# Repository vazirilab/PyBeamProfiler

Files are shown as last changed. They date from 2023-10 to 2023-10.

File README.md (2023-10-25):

# PyBeamProfiler
A laser beam profiler app for FLIR cameras to monitor laser beam and control position using stepper motors. The GUI is very easy to use and manipulate and develop. 

## Installation
1. Clone this repository
1. Install any version of the Anaconda Python distribution. We highly recommend [Miniforge](https://github.com/conda-forge/miniforge), which is minimal and fast.
1. Create a new virtual environment using the `mamba` or `conda` command that comes with Anaconda/Miniforge and the supplied `beam_profile.yml` file (top level of the repository): `mamba env create -f beam_profile.yml`
1. Activate the environment: `mamba activate beam_profile`
1. Install the package used to control the FLIR camera `PySpin` by downloading the [Spinnaker SDK library](https://www.flir.com/products/spinnaker-sdk/?vertical=machine+vision&segment=iis).
1. Run the app: `python pybeamprofiler_main.py`

## Features and Usage
- You can either use it to monitor a live stream from a FLIR camera or you can load existing data (images from previous recordings).
- The GUI gives the user control over many parameters like the number of frames or the frame rate. It also allows the user to either set a specific exposure time or change it to be automatically set.
- If the user wants to save the results of a recording, they will have to select the number of frames contained in each .csv file. The first .csv file will be named (user selected name)_0.csv and the number goes up for the next file. The .csv contains the following values: 
  1. the time a frame is acquired. 
  2. The X-position of the center. 
  3. The Y-position of the center. 
  4. The std of the Gaussian distribution of the beam. 
  5. The FWHM of the Gaussian distribution of the beam.
- The profile of the beam can be saved as well by enabling the corresponding checkbox
- If the Saving option is selected while recording from "Position Control", the saved .csv file will contain: 
  1. the timestamp of an  acquired frame.
  2. The X-position of the center. 
  3. The Y-position of the center. 
  4. Loop response in X. 
  5. Loop response in Y. 
  6. Time of frame according to PC.
- In case The user wants to add new featurs:
  1. Use [qt designer](https://doc.qt.io/qt-6/qtdesigner-manual.html) to change the Tabs files (.ui files) or add one.
  2. Change the .ui files to .py files by typing ` pyuic5 -x main.ui -o main.py` in the conda command window.
  3. Add the function or the thread to the main code and connect it to the new element you added. If you designed a new app import the class in the .py you created.
- The User can use the "Position Control" tap to control the laser with an arduino and a stepper motor. Design is in the "Hardware_design_control" folder, and the code for the arduino can be found at "src/Ard_control/Arduino_stepper_control".
- Note: Due to the camera internal memory the time stamps of the acquired frames are wrapped. Go to "pybeamprofiler\test\Unwrap_time_data.m" which is a MATLAB file that unwraps the data to time in seconds.

## Position Stabilizing Design
- In case the user wishes to use the position stabilizing design offered in the GUI, please do as follows:
  1. Go to the "pybeamprofiler\Hardware_design_control" folder and order the parts specified in "Parts_List.xlsx".
  1. Open the "Motor_mirror_mount.iam" assembly to view how the parts are Installed together and follow that scheme.
  1. The part "Stage.ipt" should be 3D printed or machined.
  1. To program the Arduino go to "pybeamprofiler\src\Ard_control\Arduino_stepper_control" and use [Arduino IDE](https://support.arduino.cc/hc/en-us/articles/360019833020-Download-and-install-Arduino-IDE) to upload the Arduino code in "Arduino_stepper_control.ino" to the Arduino
  1. Connect the stepper motor to the driver as stated in the manual of both products, and connect the pins of the driver (e.g. PUL, DIR etc) to the digital pins on the Arduino. Refer to "Arduino_stepper_control.ino" to know the correct configration of the digetal pins (e.g. PUL pin on the X-driver to PIN 8 on the Arduino etc).
  1. Connect each of the drivers to a 12V power supply. and use the switches to control the steps/revolution and current to the motors (check the manual first).
  1. Connect the Arduino to the PC and open the Position Control tab in the GUI. 
  1. You have the option to tune the PID controller and move the motors.
- The design was tested and showed reduction of slow drift and low frequency (> 0.1 Hz) movement, and, when tuned properly, can reduce high frequency movement by 5 dB. Refer to "pybeamprofiler\data\PyBeamProfiler_Poster_Shehata.pdf" for more information.

## License
Copyright (c) 2023 Mohamed Shehata

Permission is hereby granted, free of charge, to any person obtaining a copy of this software and associated documentation files (the "Software"), to deal in the Software without restriction, including without limitation the rights to use, copy, modify, merge, publish, distribute, and/or sublicense copies of the Software, and to permit persons to whom the Software is furnished to do so, subject to the following conditions:

- The above copyright notice and this permission notice shall be included in all copies or substantial portions of the Software.
- The user agrees to acknowledge the source of the SOFTWARE in any publications reporting use of it.

THE SOFTWARE IS PROVIDED "AS IS", WITHOUT WARRANTY OF ANY KIND, EXPRESS OR
IMPLIED, INCLUDING BUT NOT LIMITED TO THE WARRANTIES OF MERCHANTABILITY,
FITNESS FOR A PARTICULAR PURPOSE AND NONINFRINGEMENT. IN NO EVENT SHALL THE
AUTHORS OR COPYRIGHT HOLDERS BE LIABLE FOR ANY CLAIM, DAMAGES OR OTHER
LIABILITY, WHETHER IN AN ACTION OF CONTRACT, TORT OR OTHERWISE, ARISING FROM,
OUT OF OR IN CONNECTION WITH THE SOFTWARE OR THE USE OR OTHER DEALINGS IN THE
SOFTWARE.

## Main Developer
- Mohamed Shehata, Carl von Ossietzky Universität Oldenburg

## Acknowledgments
Special thanks to the following people for their great support and help with developing the software
- Tobias Önol-Nöbauer, Ph.D., The Rockefeller University 
- Alipasha Vaziri, Ph.D., The Rockefeller University
- Philipp Huke, Prof. Dr.-Ing., Hochschule Emden/Leer
- Lars Jepsen, M. Sc., Hochschule Emden/Leer
- Gunnar Scharf, Carl von Ossietzky Universität Oldenburg

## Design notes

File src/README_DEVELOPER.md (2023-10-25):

# Developer Guide
This file contains some description of the classes and some of the functions in the main file (pybeamprofiler\src\pybeamprofiler_main.py), and a description of the files in the src file.

## Classes
Classes are descriped from line 1 to the end of code
1. `class Thread_FLIR(QtCore.QThread):` 
  That is the thread that controls the FLIR camera. It uses many functions from the package `PySpin`, which is the camera driver provided by the [producer](https://www.flir.com/products/spinnaker-sdk/?vertical=machine+vision&segment=iis). It emits a signal to the main class when a new frame is acquired. It returns the frame, the time stamp f the frame from the camera and the number of the frame.
1. `class Thread_Data(QtCore.QThread):` 
  This thread receives names of image files from the main thread and reads them one by one. It emits a signal to the main class when a new frame is read. It returns the frame, the time stamp of the frame from the camera and the number of the frame.
1. `class Thread_motorX(QtCore.QThread):` 
  This thread is used when the Position Control is in use(refer to the readme file). It receives the number of steps and direction the motor should move, and it sends them to the Arduino through the serial port.
1. `class Thread_FLIR_Ard(QtCore.QThread):`
  This thread is used when the Position Control is in use. It works similar to `class Thread_FLIR(QtCore.QThread):` except that it returns the position of the center of mass of the image.
1. `class PyBeamProfilerGUI(QtCore.QThread):`
  This is the main thread. It controls the inputs and outputs, saves results, Interact with the user, open tabs, etc. Most of the variables, initial values, signals and slots are introduced under `def __init__(self):`. All the functions used are within this class.

## Functions
Not all the functions are mentioned here, just the unclear ones.
- `def closed_loop_start(self):` This function sets the starting point of the integral part of the PID controller in the closed loop.
- `def Follow_Position(self, FrameNP, i, TimeStamp, X_Center, Y_Center):` This function is called everytime the `class Thread_FLIR_Ard(QtCore.QThread):` thread emits a frame. It has the control loop in it.
- `def StartAcquisition_ard(self):` This function runs the `class Thread_FLIR_Ard(QtCore.QThread):` thread which starts the camera. It also Initializes the variables and changes them in case the user changed them.
- `def go_up(self):` Sends 10 steps in the up direction (depends on the camera) to the `class Thread_motorY(QtCore.QThread):` thread.
- `def Caliberate_Motors(self):` This function connects the GUI to the Arduino board, add it to the threads that control the motors, and sets the up, down, left, and right direction.
- `def ShowFrame(self, FrameNP, i, TimeStamp):` This function receives the frames from `class Thread_FLIR(QtCore.QThread):` or `class Thread_Data(QtCore.QThread):`, calculates the centroid position, find the long axis of the beam, finds the FWHM, does a gaussian fit to the log axis, and save the results if the user chooses to. This function is called everytime a signal is emitted from the threads.
- `def ShowFrame_PositionOnly(self, FrameNP, i, TimeStamp):` Works the same as `def ShowFrame(self):` except that it only measures the position using the center of mass methode. 
- `def StartAcquisition(self):`  This function runs the `class Thread_FLIR(QtCore.QThread):` thread which starts the camera or the `class Thread_Data(QtCore.QThread):` thread.
- `def gray2qimage(self, gray):` This function convert numpy array to QtImage.

## Tips
- If you wish to create and/or change a tab in the GUI use [qt designer](https://doc.qt.io/qt-6/qtdesigner-manual.html) to create a .ui file then convert it to a .py using ` pyuic5 -x main.ui -o main.py`. After that import the new file in the main code.
- If you want to add a new feature simply add it in a form of function and then se it in the main code.

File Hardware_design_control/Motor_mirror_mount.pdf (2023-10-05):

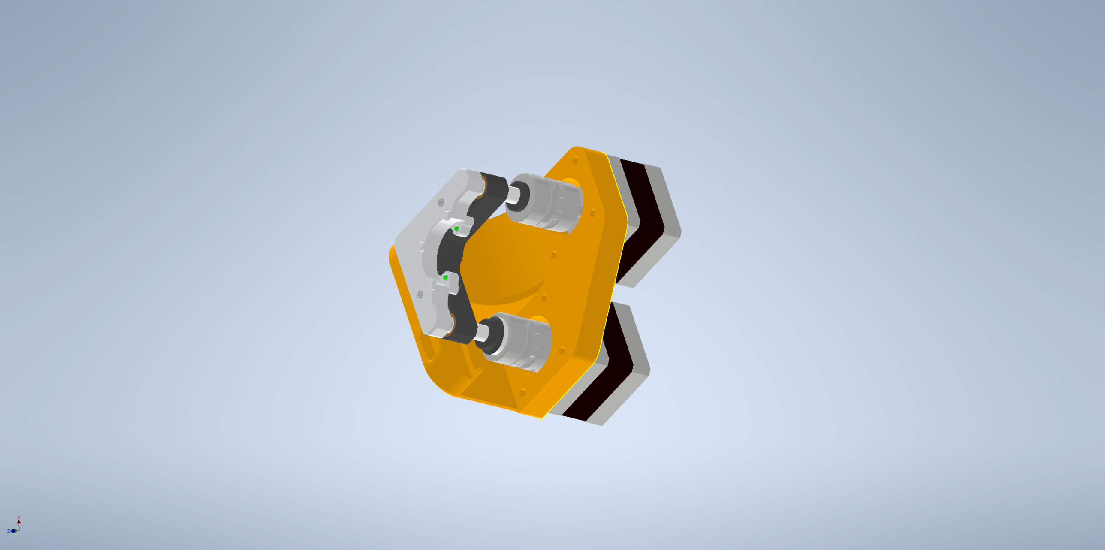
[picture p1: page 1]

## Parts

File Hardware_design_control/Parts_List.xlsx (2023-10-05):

Parts | link | Count
Nema 14 Bipolar 1.8deg 18Ncm(25.5oz.in) 0.8A 35x35x34mm 4 Wires | https://www.omc-stepperonline.com/nema-14-bipolar-1-8deg-18ncm-25-5oz-in-0-8a-5-4v-35x35x34mm-4-wires-14hs13-0804s | 2
Digital Stepper Driver 0.3-2.2A 10-30VDC for Nema 8, 11, 14, 16, 17 Stepper Motor | https://www.omc-stepperonline.com/digital-stepper-driver-0-3-2-2a-10-30vdc-for-nema-8-11-14-16-17-stepper-motor-dm320t | 2
Arduino Mega 2560 Rev3 | https://store.arduino.cc/products/arduino-mega-2560-rev3 | 1
Set Screw High-Parallel-Misalignment Flexible Shaft Couplings | https://www.mcmaster.com/catalog/129/1449/59985K14 | 2
KM1CE - Ø1" Clear-Edge Kinematic Mirror Mount, 2 Adjusters | https://www.thorlabs.com/thorproduct.cfm?partnumber=KM1CE | 1
Teledyne FLIR FFY-U3-04S2M-S | https://www.loretech.io/products/teledyne-flir-ffy-u3-04s2m-s?variant=41921567195312&currency=USD | 1

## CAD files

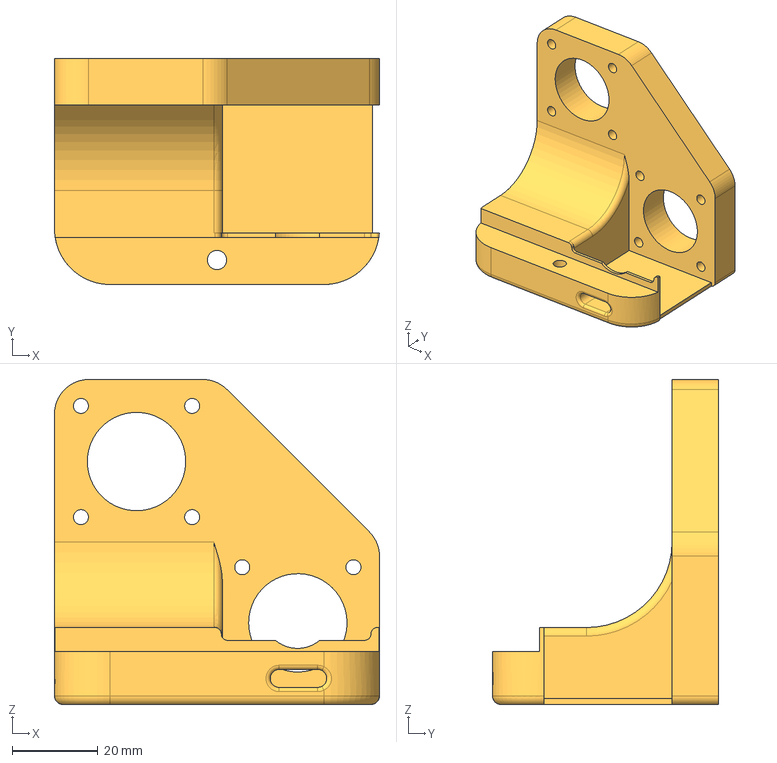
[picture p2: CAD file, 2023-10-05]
Hardware_design_control/Stage.stp
76.0 x 52.9 x 76.0 mm

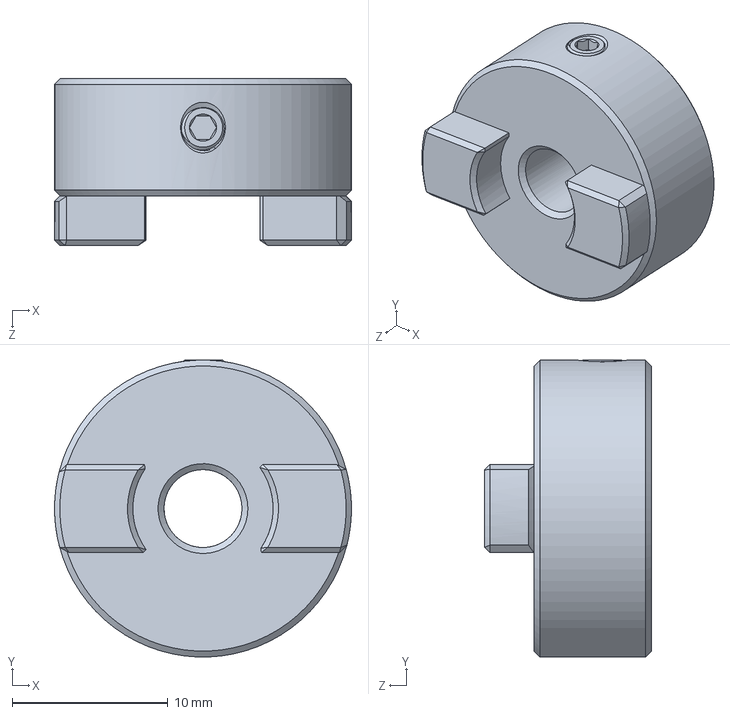
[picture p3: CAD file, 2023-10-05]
Hardware_design_control/59985K202_High-Parallel-Misalignment Flexible Shaft Coupling.SLDPRT
19.1 x 19.0 x 10.7 mm

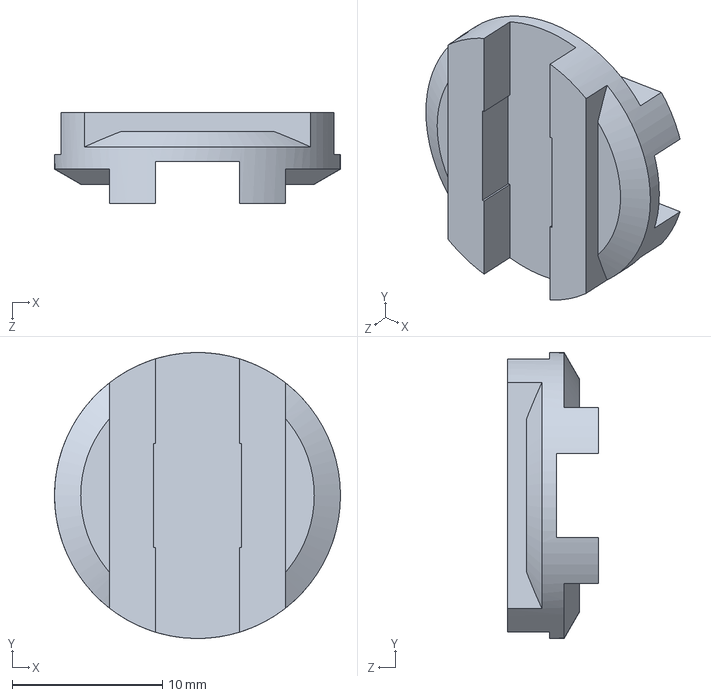
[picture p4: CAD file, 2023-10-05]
Hardware_design_control/59985K62_93 in.-lbs. Acetal Disc for 3 4 OD High-Parallel-Misalignment Flexible Shaft Coupling.SLDPRT
19.1 x 19.1 x 6.05 mm

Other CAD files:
Hardware_design_control/59985K14_High-Parallel-Misalignment Flexible Shaft Coupling.SLDPRT
Hardware_design_control/59985K14_High-Parallel-Misalignment Flexible Shaft Coupling/59985K14_High-Parallel-Misalignment Flexible Shaft Coupling.ipt
Hardware_design_control/59985K202_High-Parallel-Misalignment Flexible Shaft Coupling/59985K202_High-Parallel-Misalignment Flexible Shaft Coupling.ipt
Hardware_design_control/59985K62_93 in.-lbs. Acetal Disc for 3 4 OD High-Parallel-Misalignment Flexible Shaft Coupling/59985K62_93 in.-lbs. Acetal Disc for 3 4 OD High-Para.ipt
Hardware_design_control/KM1CE-Step.ipt
Hardware_design_control/Knob_adp.ipt
Hardware_design_control/Motor_mirror_mount.iam
Hardware_design_control/OldVersions/Motor_mirror_mount.0018.iam
Hardware_design_control/Stage.dwg
Hardware_design_control/Stage.ipt
Hardware_design_control/stepper.ipt

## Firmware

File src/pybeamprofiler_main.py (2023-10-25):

import PyQt5.QtWidgets
from PyQt5.QtWidgets import *
from PyQt5 import uic
# from PyQt5.QtGui import QPixmap, QImage
from PyQt5 import QtGui, QtCore
import skimage
import numpy as np
import sys
import glob
import os
import PIL
from PIL import ImageFilter, Image
import math
import time
import scipy as sp
import PySpin
from View_page import Ui_MainWindow
from Offline_viewer import Ui_Ofline_Viewer
from Arduino_Control import Ui_Arduino_Control
from Tunning import Ui_Tunning_parameters
import pyqtgraph as pg
import pyfirmata
import serial
import serial.tools.list_ports
import warnings

# A thread for the camera. It emits frames, the number of the current frame and the time stamp
class Thread_FLIR(QtCore.QThread):
    changePixmap_FLIR = QtCore.pyqtSignal(np.ndarray, int, int) # a signal to renew each frame
    # those values are initial numbers that will be redefined in the GUI
    # initial values
    NUM_IMG = 100000
    serial = '20270803'  # seriel of the flir cam
    ppmm = 0.0069  # pixels per mm to convert position to mm
    ppmm = 1 / ppmm
    frame_rate = 50.0
    ExpTime_us = 8000
    Stop_Loop = False
    file_names = None
    Auto_ExpTimeCond = False
    is_running = False
    def run(self):
        self.is_running = True
        self.system = PySpin.System.GetInstance()  # Retrieve singleton reference to system object
        self.version = self.system.GetLibraryVersion()  # Get current library version
        self.cam_list = self.system.GetCameras()  # Retrieve list of cameras from the system
        self.cam = self.cam_list.GetBySerial(self.serial)
        sNodemap = self.cam.GetTLStreamNodeMap() #change the streaming mode to acquire new frames only
        node_bufferhandling_mode = PySpin.CEnumerationPtr(sNodemap.GetNode('StreamBufferHandlingMode'))
        node_newestonly = node_bufferhandling_mode.GetEntryByName('NewestOnly')
        node_newestonly_mode = node_newestonly.GetValue()
        node_bufferhandling_mode.SetIntValue(node_newestonly_mode)
        self.nodemap_tldevice = self.cam.GetTLDeviceNodeMap()
        self.cam.Init()
        self.nodemap = self.cam.GetNodeMap()
        self.node_acquisition_mode = PySpin.CEnumerationPtr(self.nodemap.GetNode('AcquisitionMode'))
        self.node_acquisition_mode_continuous = self.node_acquisition_mode.GetEntryByName('Continuous')
        self.acquisition_mode_continuous = self.node_acquisition_mode_continuous.GetValue()
        self.node_acquisition_mode.SetIntValue(self.acquisition_mode_continuous)
        self.processor = PySpin.ImageProcessor()
        self.cam.BeginAcquisition()
        self.cam.ExposureTime.SetValue(self.ExpTime_us)
        self.cam.AcquisitionFrameRateEnable.SetValue(True)
        self.cam.AcquisitionFrameRate.SetValue(self.frame_rate)
        i = 0
        while i <= (self.NUM_IMG - 1):
            if self.Stop_Loop:
                break

            image_result = self.cam.GetNextImage(10000)  # capturing a frame
            FrameNP = image_result.GetNDArray()  # get the result as a numpy array
            TimeStamp = image_result.GetTimeStamp()
            if np.max(FrameNP) > 20:  # prevent gui from crashing when laser off

                # setting Auto exposure time mode
                if self.Auto_ExpTimeCond and np.max(FrameNP) > 240:

                    self.ExpTime_us = self.ExpTime_us - 50
                    self.cam.ExposureTime.SetValue(self.ExpTime_us)
                    image_result = self.cam.GetNextImage(10000)  # capturing a frame
                    FrameNP = image_result.GetNDArray()  # get the result as a numpy array
                    time.sleep(0.01)


                elif np.max(FrameNP) < 220 and self.Auto_ExpTimeCond:

                    self.ExpTime_us = self.ExpTime_us + 50
                    self.cam.ExposureTime.SetValue(self.ExpTime_us)
                    image_result = self.cam.GetNextImage(10000)  # capturing a frame
                    FrameNP = image_result.GetNDArray()  # get the result as a numpy array
                    time.sleep(0.01)

                self.changePixmap_FLIR.emit(FrameNP, i, TimeStamp)  # send the frame and the current frame number to the GUI
                i = i + 1
                image_result.Release()
            else:
                print(f"No laser detected, Please turn on the laser. \n")
                while True:
                    image_result = self.cam.GetNextImage(10000)  # capturing a frame
                    FrameNP = image_result.GetNDArray()  # get the result as a numpy array
                    time.sleep(0.01)
                    image_result.Release()
                    if np.max(FrameNP) > 20:
                        if i == 0:
                            print(f"Laser detected. \n ")
                            break
                        else:
                            print(f"Laser detected. \n ")
                            i = i - 1
                            break

                    if self.Stop_Loop:
                        break

            time.sleep(0.01)

        self.cam.EndAcquisition()
        self.cam.DeInit()
        self.is_running = False


# A thread that reads and emits images of a laser beam to imitate an accusation process
class Thread_Data(QtCore.QThread):
    changePixmap_Data = QtCore.pyqtSignal(np.ndarray, int, float)# a signal to renew each frame
    # those values are initial numbers that will be redefined in the GUI
    NUM_IMG = 100000
    serial = '20270803'  # seriel of the flir cam
    ppmm = 0.0069  # pixels per mm to convert position to mm
    ppmm = 1 / ppmm
    frame_rate = 50.0
    ExpTime_us = 8000
    Stop_Loop = False
    file_names = None
    Auto_ExpTimeCond = False
    is_running = False
    def run(self):
        self.is_running = True
        file_Nr = len(self.file_names)
        for i in range(file_Nr):
            FrameNP = skimage.io.imread(self.file_names[i])  # get the result as a numpy array
            t = time.time()
            if self.Stop_Loop:
                break
            time.sleep(1 / self.frame_rate)
            self.changePixmap_Data.emit(FrameNP, i, t)  # send the frame and the current frame number to the GUI
        self.is_running = False

# Threads to send signals to an Arduino to stabilize the position of the beam
class Thread_motorX(QtCore.QThread):
    board=0
    direction=0
    DIR_PIN=3
    PUL_PIN=2
    steps = 40
    is_running = False

    def __init__(self,parent=None):
        super(Thread_motorX, self).__init__(parent)

    def run(self):
        self.is_running = True
        # Set the direction (HIGH for clockwise, LOW for counterclockwise).
        command = f"X,{self.direction},{(self.steps)}\n"
        try:
            self.board.write(command.encode())

        except:
            pass

        self.is_running = False


class Thread_motorY(QtCore.QThread):
    board=0
    direction=0
    DIR_PIN=3
    PUL_PIN=2
    steps = 40
    directionX = 0
    is_running = False
    def __init__(self,parent=None):
        super(Thread_motorY, self).__init__(parent)

    def run(self):
        self.is_running = True
        # Set the direction (HIGH for clockwise, LOW for counterclockwise).
        self.is_running = True
        # Set the direction (HIGH for clockwise, LOW for counterclockwise).
        command = f"Y,{self.direction},{(self.steps)}\n"
        try:
            self.board.write(command.encode())
            
        except:
            pass

        self.is_running = False


# Thread to read frames from a FLIR camera and get the center of mass (The position of the laser). the signal is then
# sent to the control loop to correct for the position
class Thread_FLIR_Ard(QtCore.QThread):
    changePixmap_FLIR = QtCore.pyqtSignal(np.ndarray, int, int, float, float) # a signal to renew each frame
    # those values are initial numbers that will be redefined in the GUI
    NUM_IMG = 100000
    serial = '20270803'  # seriel of the flir cam
    ppmm = 0.0069  # pixels per mm to convert position to mm
    ppmm = 1 / ppmm
    frame_rate = 50.0
    ExpTime_us = 8000
    Stop_Loop = False
    file_names = None
    Auto_ExpTimeCond = False
    is_running = False
    def run(self):
        self.is_running = True
        self.system = PySpin.System.GetInstance()  # Retrieve singleton reference to system object
        self.version = self.system.GetLibraryVersion()  # Get current library version
        self.cam_list = self.system.GetCameras()  # Retrieve list of cameras from the system
        self.cam = self.cam_list.GetBySerial(self.serial)
        sNodemap = self.cam.GetTLStreamNodeMap() #change the streaming mode to acquire new frames only
        node_bufferhandling_mode = PySpin.CEnumerationPtr(sNodemap.GetNode('StreamBufferHandlingMode'))
        node_newestonly = node_bufferhandling_mode.GetEntryByName('NewestOnly')
        node_newestonly_mode = node_newestonly.GetValue()
        node_bufferhandling_mode.SetIntValue(node_newestonly_mode)
        self.nodemap_tldevice = self.cam.GetTLDeviceNodeMap()
        self.cam.Init()
        self.nodemap = self.cam.GetNodeMap()
        self.node_acquisition_mode = PySpin.CEnumerationPtr(self.nodemap.GetNode('AcquisitionMode'))
        self.node_acquisition_mode_continuous = self.node_acquisition_mode.GetEntryByName('Continuous')
        self.acquisition_mode_continuous = self.node_acquisition_mode_continuous.GetValue()
        self.node_acquisition_mode.SetIntValue(self.acquisition_mode_continuous)
        self.processor = PySpin.ImageProcessor()
        self.cam.BeginAcquisition()
        self.cam.ExposureTime.SetValue(self.ExpTime_us)
        self.cam.AcquisitionFrameRateEnable.SetValue(True)
        self.cam.AcquisitionFrameRate.SetValue(self.frame_rate)
        i = 0
        while i <= (self.NUM_IMG - 1):
            if self.Stop_Loop:
                break

            image_result = self.cam.GetNextImage(10000)  # capturing a frame
            FrameNP = image_result.GetNDArray()  # get the result as a numpy array
            TimeStamp = image_result.GetTimeStamp()
            if np.max(FrameNP) > 20:  # prevent gui from crashing when laser off

                # setting Auto exposure time mode
                if self.Auto_ExpTimeCond and np.max(FrameNP) > 240:

                    self.ExpTime_us = self.ExpTime_us - 100
                    self.cam.ExposureTime.SetValue(self.ExpTime_us)
                    image_result = self.cam.GetNextImage(10000)  # capturing a frame
                    FrameNP = image_result.GetNDArray()  # get the result as a numpy array
                    time.sleep(0.01)


                elif np.max(FrameNP) < 120 and self.Auto_ExpTimeCond:

                    self.ExpTime_us = self.ExpTime_us + 50
                    self.cam.ExposureTime.SetValue(self.ExpTime_us)
                    image_result = self.cam.GetNextImage(10000)  # capturing a frame
                    FrameNP = image_result.GetNDArray()  # get the result as a numpy array
                    time.sleep(0.01)
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

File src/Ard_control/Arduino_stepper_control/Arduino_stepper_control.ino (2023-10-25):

// In this skitch you can change the pin numbers for PUL and DIR to suit your Arduino.
// Stepper 1 is for the x direction and 2 is for the y direction

const int ENA1 = 4;
const int OPTO1 = 5;
const int ENA2 = 10;
const int OPTO2 = 11;
const int PUL1 = 2;
const int DIR1 = 3;
const int PUL2 = 8;
const int DIR2= 9;
int  direction,steps;
char motor;
//char motor = 'X';
//int direction = 0;
//int steps = 0;
 //AccelStepper stepper1(AccelStepper::DRIVER, 2, 3); // 2 is for PUL and 3 is for DIR
 //AccelStepper stepper2(AccelStepper::DRIVER, 8, 9); 
void setup() {
  // put your setup code here, to run once:
  Serial.begin(115200);
  pinMode(ENA1, OUTPUT);
  pinMode(OPTO1, OUTPUT);
  pinMode(PUL1, OUTPUT);
  pinMode(DIR1, OUTPUT);
  pinMode(PUL2, OUTPUT);
  pinMode(DIR2, OUTPUT);
  pinMode(ENA2, OUTPUT);
  pinMode(OPTO2, OUTPUT);
  digitalWrite(OPTO1, HIGH);
  digitalWrite(OPTO2, HIGH);
  digitalWrite(ENA1, HIGH);
  digitalWrite(ENA2, HIGH);
  delay(1);
//  stepper1.setMaxSpeed(3000000);
  //stepper2.setMaxSpeed(3000000);
//  stepper2.setSpeed(2800);
//  stepper1.setSpeed(2800);
//  stepper1.setAcceleration(1000000.0);
 // stepper2.setAcceleration(1000000.0);
//  stepper1.setMinPulseWidth(10);
  //stepper2.setMinPulseWidth(10);
  
  digitalWrite(13, LOW);
}

void loop() {
  
  if (Serial.available() > 0) {
    String command = Serial.readStringUntil('\n'); // Read the command from Python
    
    
    sscanf(command.c_str(), "%c,%d,%d", &motor, &direction, &steps);
    
    if (motor == 'X') {
      
 //     if (stepper1.isRunning()) {
   //     stepper1.stop();
     //   stepper1.runToPosition();
        
   //   }
      
      if (direction == 0) {
        digitalWrite(3, LOW);
        delayMicroseconds(50);
        //int s = (steps.toInt());
        for (int i = 1; i <= steps; i++) {
           delayMicroseconds(8);
           digitalWrite(2, HIGH);
           delayMicroseconds(8);
           digitalWrite(2, LOW);
           
      }
        

      }else if (direction == 1) {
        //int s = (steps);
        
        digitalWrite(3, HIGH);
        delayMicroseconds(50);
        //int s = (steps.toInt());
        for (int i = 1; i <= steps; i++) {
           delayMicroseconds(8);
           digitalWrite(2, HIGH);
           delayMicroseconds(8);
           digitalWrite(2, LOW);
           
        }
        
      }
      
      
 //     for (int i = 0; i <= 255; i++) {
 //          delayMicroseconds(1000);
 //          digitalWrite(2, HIGH);
 //          delayMicroseconds(1000);
 //          digitalWrite(2, LOW);
  //    }
 //     for (int i = 0; i <= 255; i++) {
 //          delayMicroseconds(1000);
 //          digitalWrite(8, HIGH);
 //          delayMicroseconds(1000);
 //          digitalWrite(8, LOW);
 //     }

  }else if (motor == 'Y') {
 //     if (stepper2.isRunning()) {
   //     stepper2.stop();
     //   stepper2.runToPosition();
        
   //   }
      if (direction == 0) {
        digitalWrite(9, LOW);
        delayMicroseconds(50);
        for (int i = 1; i <= steps; i++) {
           delayMicroseconds(8);
           digitalWrite(8, HIGH);
           delayMicroseconds(8);
           digitalWrite(8, LOW);
           
        }
        
      }else if (direction == 1) {
        digitalWrite(9, HIGH);
        delayMicroseconds(50);
        for (int i = 1; i <= steps; i++) {
           delayMicroseconds(8);
           digitalWrite(8, HIGH);
           delayMicroseconds(8);
           digitalWrite(8, LOW);
           
        }

      }
      
      
    }
  }else if (motor == 'B') {
    for (int i = 0; i < 20; i++){
      delay(0.5);
      digitalWrite(13, HIGH);
      delay(0.5);
      digitalWrite(13, LOW);
    }
  }
 // stepper1.runSpeedToPosition();
  //stepper2.runSpeedToPosition();

  // put your main code here, to run repeatedly:

}

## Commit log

2023-06-14 Fix the const. for thread class
2023-06-26 Control frame rate added
2023-06-28 remove print command
2023-06-29 different Threads for stream option
2023-07-18 adding files for installing
    [prev_data0.csv, prev_dataLong axis plot0.csv]
2023-07-28 prevent gui from crashing when laser off
2023-08-09 adding frame rate and fixing the time stamp
2023-08-15 option to control mirror with arduino
2023-08-15 update control mirror with arduino
2023-10-05 folder design
    [prev_data0.csv, prev_dataLong axis plot0.csv]
2023-10-05 hardware design
    [Motor_mirror_mount.0017.iam, Motor_mirror_mount.iam]
2023-10-05 hardware design parts
    [Parts_List.xlsx]
2023-10-05 hardware design parts and readme
    [Parts_List.xlsx]
